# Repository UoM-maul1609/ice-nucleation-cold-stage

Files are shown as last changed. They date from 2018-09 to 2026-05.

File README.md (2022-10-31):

# Ice Nucleation Cold Stage

The Ice Nucleation Cold Stage (INCS) is a project using an Arduino and Raspberry Pi to control a Peltier module to cool and film droplets to the point where they freeze. 

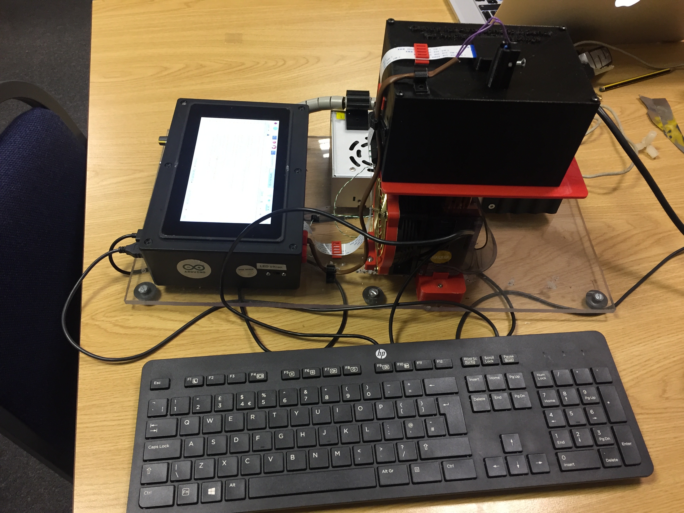
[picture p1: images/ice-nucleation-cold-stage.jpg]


<em>The Ice Nucleation Cold Stage on a desk.</em>

# Table of contents
1. [Overview](#overview)
1. [Buck Converter](#buck-conv)
2. [Dependencies](#Dependencies)
3. [Folder structure](#Folder-Structure)
5. [Contributing](#Contributing)
6. [Code of Conduct](#Code-of-Conduct)

## Overview 

The electronics fits in a project box, with a touchscreen, enabling ease of transport in the field.

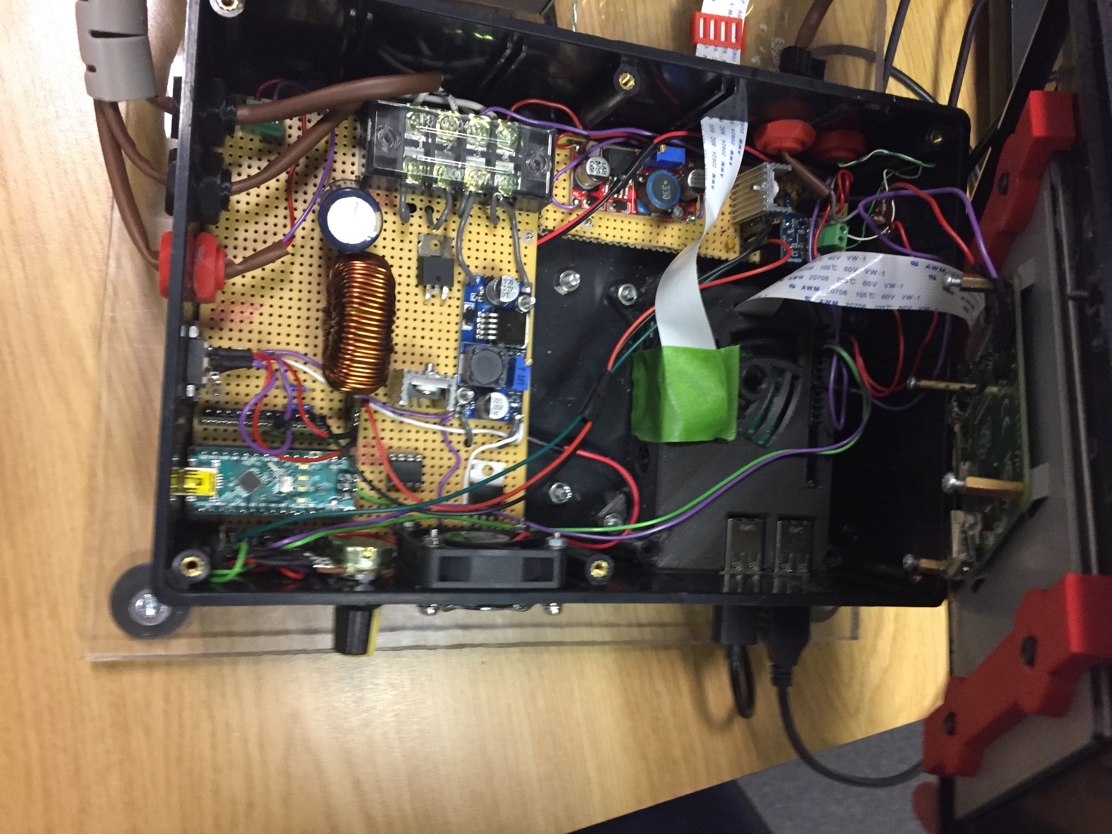
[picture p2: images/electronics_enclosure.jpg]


<em>Peltier circuit inside the project box.</em>

In addition most of the other parts are 3-d printed.

## Buck Converter 
A substantial part of this project is the buck converter circult, which is controlled by an Arduino using pulse width modulation. A buck converter is required to control the Peltier module because Peltier modules require a smooth input voltage. Pulse width modulation alone is not sufficient. 

The circuit is based on a so-called low-side switch design, meaning the MosFET switch is on the "low-side" of the load [see here](images/high_side_n_channel_buck_converter.png).

The circuit for the buck converter is shown below.

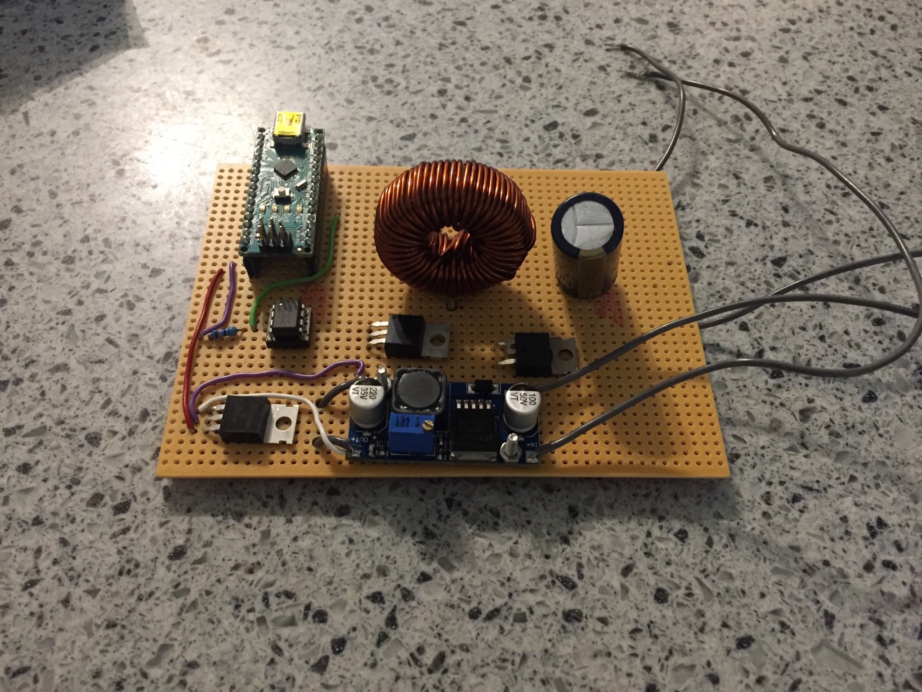
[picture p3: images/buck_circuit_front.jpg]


<em>Buck converter circuit. It consists of an Arduino Nano; a gate driver; MosFET, Inductor, Capactor, and Schottky diode. In addition there is a 3 A buck converter and linear regulator to power the arduino from a DC input.</em>

## Dependencies 

I needed to install a library for the Arduino for PID control. The library is: PID controller by Brett Beaugard. I also had to use "Wire.h" (installed by default) .for I2C communication between the Raspberry Pi and Arduino.

For the Raspberry PI the following python libraries were used: smbus; struct; time; numpy.

## Folder structure 

The repository structure is now discussed

### Directory layout

    .                           
    ├── arduino               # code for the Arduino
    ├── images                # image files for the project
    ├── links                 # some links that I used 
    ├── matlab                # matlab files (e.g. to process video to get freezing events)
    ├── openSCAD              # Design files in openSCAD
    ├── python                # Raspberry Pi files to do temperature ramps, etc
    ├── README.md             # This readme
    └── stl						# stl design files
    
----------

**REQUIRED PARTS**

In order to **make your own Ice Nucleation Cold Stage**, you may use the **part list below** to acquire all the components **on your own**. Note, although Amazon is suggested, I often used a company supplier, which was cheaper.

<table style="width:100%">
  <tr> 
    <td>
    Raspberry Pi 3 7 inch touchscreen <br>
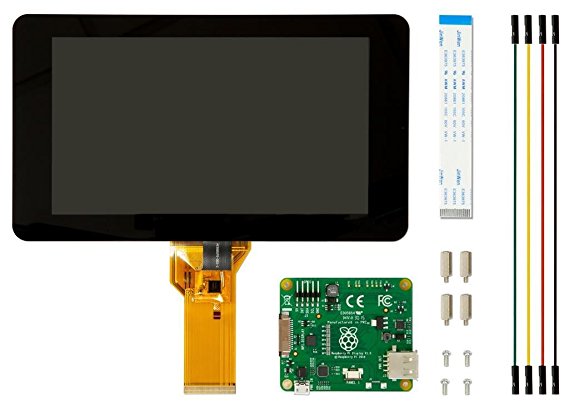
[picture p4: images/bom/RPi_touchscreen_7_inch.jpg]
    </td>
    <td><a href="https://www.amazon.co.uk/Raspberry-Pi-7-Inch-Screen-Display/dp/B014WKCFR4/ref=sr_1_3?ie=UTF8&qid=1531558042&sr=8-3&keywords=raspberry+pi+touch+screen+7+inch" target="_blank"> Amazon </a></td> 
    <td>£63</td>
  </tr>
  
  <tr> 
    <td>
    Raspberry Pi 3 b+ <br>
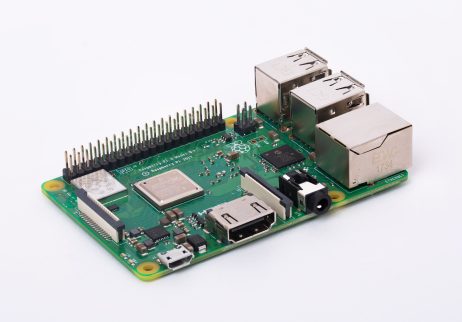
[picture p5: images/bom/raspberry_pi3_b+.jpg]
    </td>
    <td><a href="https://www.amazon.co.uk/Raspberry-Pi-Model-64-Bit-Processor/dp/B07BDR5PDW/ref=sr_1_3?ie=UTF8&qid=1531556638&sr=8-3&keywords=raspberry-pi+3+b" target="_blank"> Amazon </a></td> 
    <td>£35</td>
  </tr>
  
  <tr> 
    <td>
    Raspberry Pi Camera Board 8 Megapixel Version 2 1080p <br>
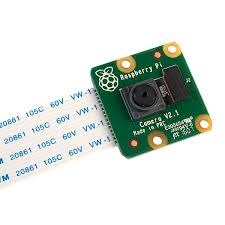
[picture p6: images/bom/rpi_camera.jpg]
    </td>
    <td><a href="https://www.rapidonline.com/raspberry-pi-camera-board-8-megapixel-version-2-1080p-75-0530" target="_blank"> Rapid Online </a></td> 
    <td>£23.70</td>
  </tr>

  <tr>
    <td>
    Arduino Nano A000005 Board V3<br>
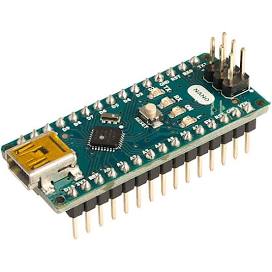
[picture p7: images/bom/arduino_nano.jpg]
    </td>
    <td><a href="https://www.rapidonline.com/arduino-nano-a000005-board-v3-73-4448" target="_blank"> Rapid Electronics </a></td> 
    <td>£15.60</td>
  </tr>

  <tr>
    <td>
    2.54mm Pitch Vertical 8 Way, Through Hole Turned pin Open Frame IC Dip Socket, 5A<br>
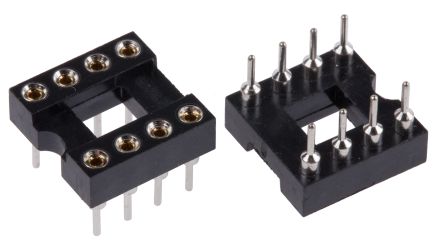
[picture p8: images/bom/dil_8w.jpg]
    </td>
    <td><a href="https://uk.rs-online.com/web/p/dil-sockets/0813115/" target="_blank"> RS Components </a></td> 
    <td>£0.38</td>
  </tr>

  <tr>
    <td>
    Rapid Stripboard 95 x 127mm (x2)<br>
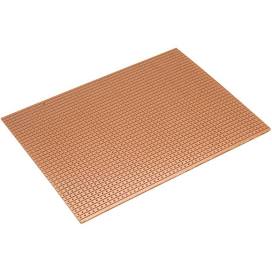
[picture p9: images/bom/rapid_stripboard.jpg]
    </td>
    <td><a href="https://www.rapidonline.com/rapid-stripboard-95-x-127mm-34-0515" target="_blank"> Rapid Online </a></td> 
    <td>£3.84</td>
  </tr>

  <tr>
    <td>
    2200 uF capactor, 35V.<br>
    </td>
    <td><a href="https://uk.farnell.com/panasonic-electronic-components/eca1vhg222/cap-alu-elec-2200uf-35v-rad/dp/1848552?st=CAPACITOR,%202200UF%2035V;%20Automotive%20Qualification%20Standard:AEC-Q200" target="_blank"> Farnell </a></td> 
    <td>£1.27</td>
  </tr>

  <tr>
    <td>
    470 µH, 7A, 0.064 ohm, ± 20%, Inductor<br>
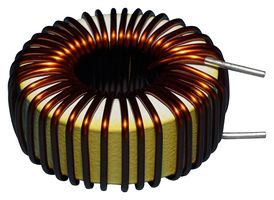
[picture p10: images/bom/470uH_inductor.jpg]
    </td>
    <td><a href="https://uk.farnell.com/abracon/atca-08-471m-v/inductor-470uh-7a-20-radial/dp/2665051?krypto=pY3JNPCYatNk0vDDUf4Tn9JLFiz93rvd2B4Xt3Ip1h5SCi3yEomoX%2BUEleAGflP2kAMSJSf9N%2FZLG3PFYvM%2Bmw%3D%3D&ddkey=https%3Aen-GB%2FElement14_United_Kingdom%2Fsearch" target="_blank"> Farnell </a></td> 
    <td>£9.89</td>
  </tr>

  <tr>
    <td>
    IRF520NPBF -  MOSFET Transistor, N Channel <br>
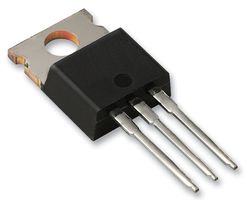
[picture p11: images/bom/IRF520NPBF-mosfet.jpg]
    </td>
    <td><a href="https://uk.farnell.com/infineon/irf520npbf/mosfet-n-100v-9-7a-to-220ab/dp/9103031" target="_blank"> Farnell </a></td> 
    <td>£0.65</td>
  </tr>

  <tr>
    <td>
    VS-15TQ060PBF -  Schottky Rectifier <br>
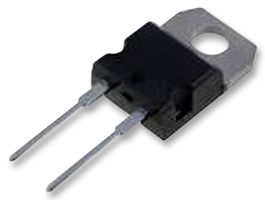
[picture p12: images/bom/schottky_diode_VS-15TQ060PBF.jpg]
    </td>
    <td><a href="https://uk.farnell.com/vishay-semiconductor/vs-15tq060pbf/diode-schottky-15a-60v-to-220ac/dp/8657009" target="_blank"> Farnell </a></td> 
    <td>£2.05</td>
  </tr>

  <tr>
    <td>
    Cooler Master Hyper TX (RR-PCH-s9U1-GP) <br>
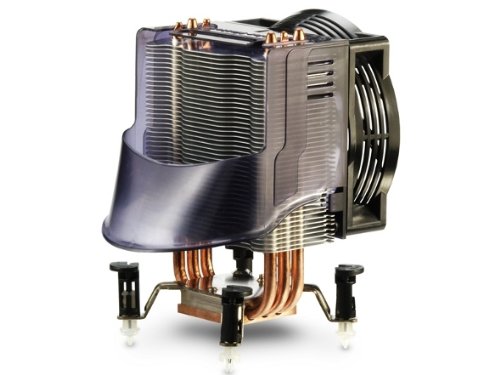
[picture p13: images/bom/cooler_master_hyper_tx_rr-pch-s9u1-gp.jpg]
    </td>
    <td><a href="https://www.amazon.co.uk/Cooler-Master-Socket-775-650-1800RPM-41-76-CFM/dp/B000K0ZSH0" target="_blank"> This was given to me. It is discontinued, but any similar heat sink could be used (e.g. the Cooler Master Hyper TX3i) </a></td> 
    <td>approx. £30</td>
  </tr>

  <tr>
    <td>
    mc34152 Gate Driver <br>
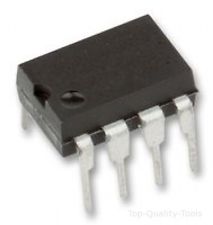
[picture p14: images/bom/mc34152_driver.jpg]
    </td>
    <td><a href="https://uk.rs-online.com/web/p/mosfet-power-drivers/5165506/" target="_blank"> RS Components </a></td> 
    <td>£1.15</td>
  </tr>

  <tr>
    <td>
    Enclosure <br>
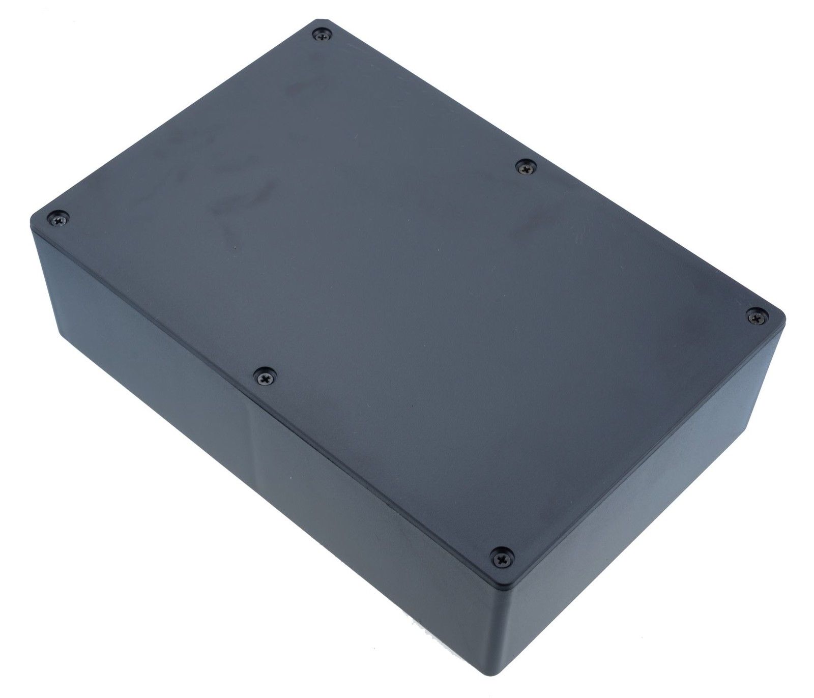
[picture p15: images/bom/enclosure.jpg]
    </td>
    <td><a href="https://www.ebay.co.uk/itm/1591XXFSBK-Genuine-Hammond-Black-ABS-Enclosure-Box-221-x-150-x-63mm/262220045766?hash=item3d0d885dc6:g:-PkAAOSw1BlZVgdG" target="_blank"> Ebay </a></td> 
    <td>£10</td>
  </tr>

  <tr>
    <td>
    Micro SD card<br>
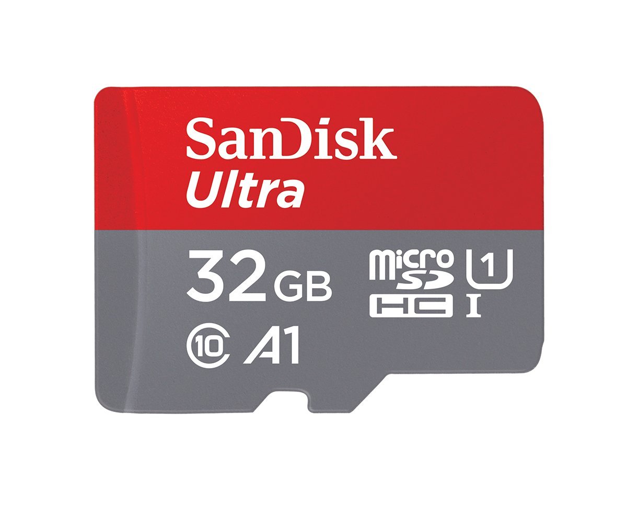
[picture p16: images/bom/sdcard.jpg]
    </td>
    <td><a href="https://www.amazon.co.uk/gp/offer-listing/B073JWXGNT/ref=sr_1_5_olp?s=electronics-accessories&ie=UTF8&qid=1531613685&sr=1-5&keywords=micro+sd+card" target="_blank"> Amazon </a></td> 
    <td>£8</td>
  </tr>

  <tr>
    <td>
    2 Pin 5 mm Pinch PCB Mount Screw Terminal Block Connector<br>
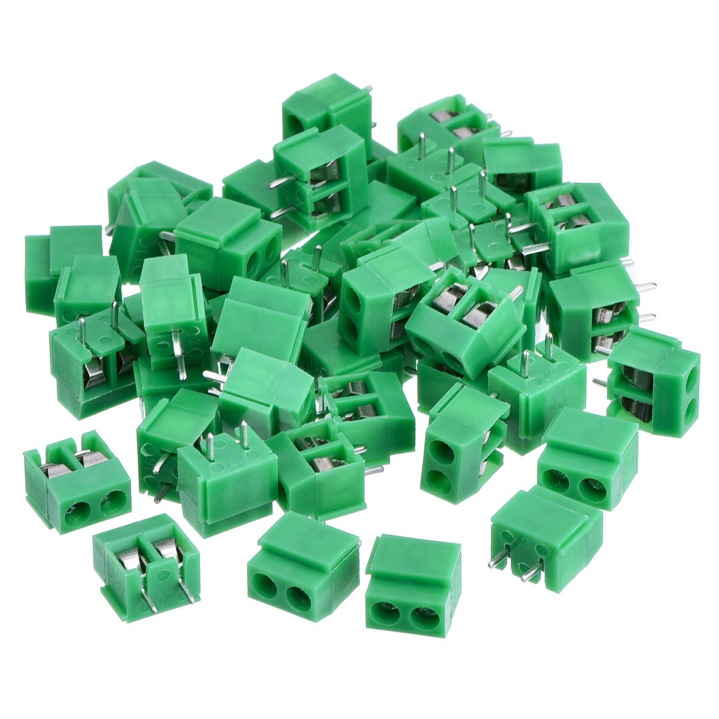
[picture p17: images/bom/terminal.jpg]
    </td>
    <td><a href="https://www.amazon.co.uk/gp/product/B01MT4LC0F/ref=oh_aui_detailpage_o03_s00?ie=UTF8&psc=1" target="_blank"> Amazon </a></td> 
    <td>£6</td>
  </tr>

  <tr>
    <td>
    Buck converter <br>
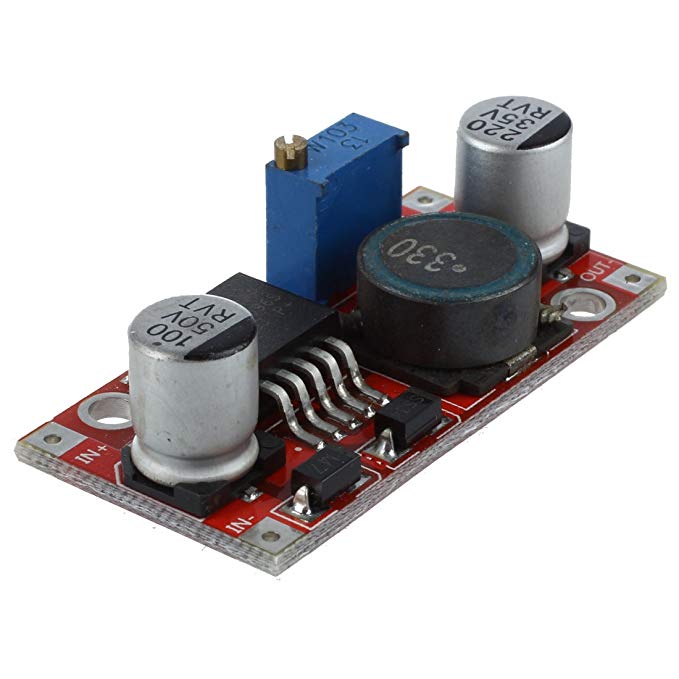
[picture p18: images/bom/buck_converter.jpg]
    </td>
    <td><a href="https://www.amazon.co.uk/gp/product/B00K67XSYC/ref=oh_aui_detailpage_o06_s00?ie=UTF8&psc=1" target="_blank"> Amazon </a></td> 
    <td>£8</td>
  </tr>

  <tr>
    <td>
    Linear regulator 10V, 1A<br>
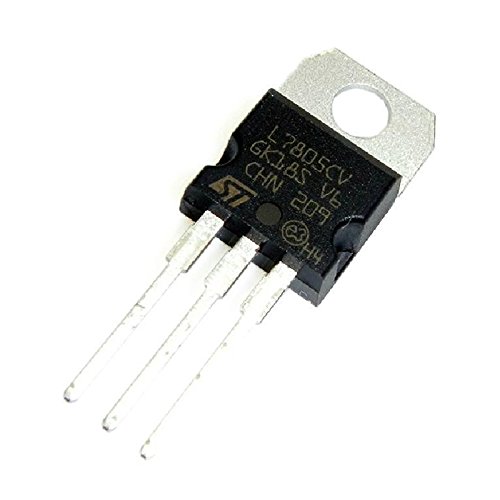
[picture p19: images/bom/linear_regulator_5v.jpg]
    </td>
    <td><a href="https://uk.farnell.com/on-semiconductor/ka7810etu/linear-volt-reg-1a-10v-to-220ab/dp/2451046" target="_blank"> Farnell </a></td> 
    <td>£3</td>
  </tr>
  
  <tr>
    <td>
    Slide switch <br>
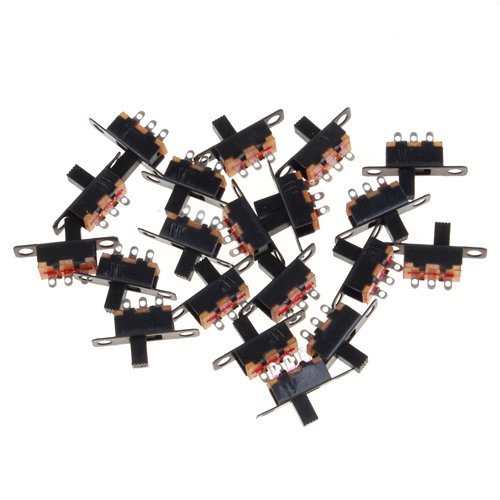
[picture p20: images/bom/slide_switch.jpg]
    </td>
    <td><a href="https://www.amazon.co.uk/gp/product/B008R50AA0/ref=oh_aui_detailpage_o07_s00?ie=UTF8&psc=1" target="_blank"> Amazon </a></td> 
    <td>£0.15</td>
  </tr>
  
  <tr>
    <td>
    PCB Header Connectors <br>
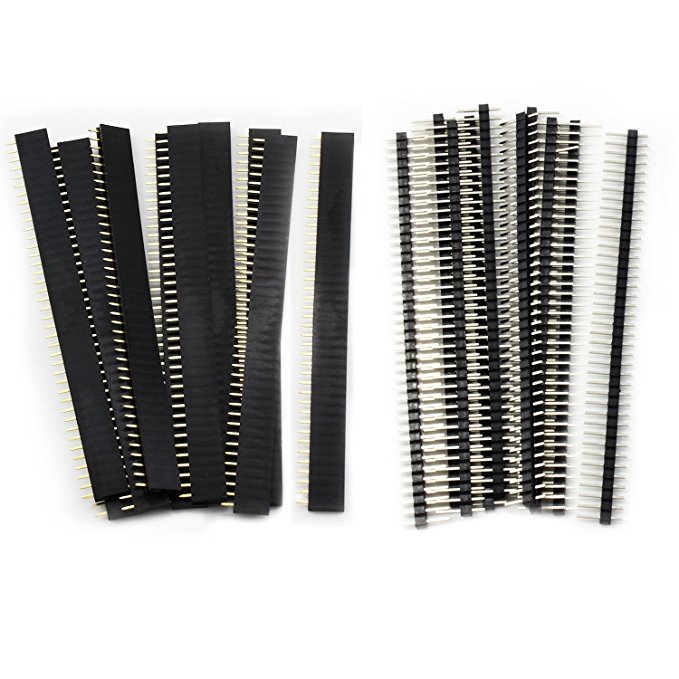
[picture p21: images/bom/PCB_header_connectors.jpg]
    </td>
    <td><a href="https://www.amazon.co.uk/gp/product/B01M69EA9O/ref=oh_aui_detailpage_o03_s00?ie=UTF8&psc=1" target="_blank"> Amazon </a></td> 
    <td>£5</td>
  </tr>
  
  <tr>
    <td>
    Dupoint wires <br>
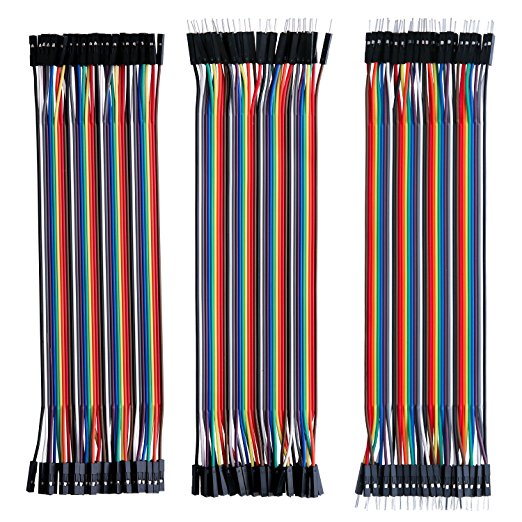
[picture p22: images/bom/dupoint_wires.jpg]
    </td>
    <td><a href="https://www.amazon.co.uk/gp/product/B01EV70C78/ref=oh_aui_detailpage_o04_s00?ie=UTF8&psc=1" target="_blank"> Amazon </a></td> 
    <td>£6</td>
  </tr>
  
  <tr>
    <td>
    20AWG Wire <br>
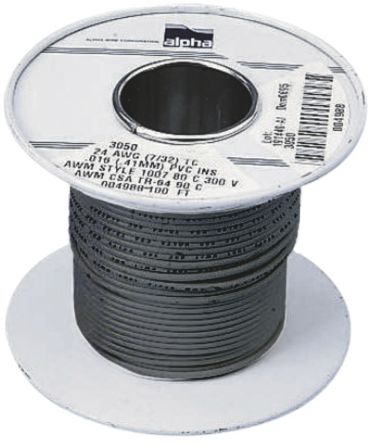
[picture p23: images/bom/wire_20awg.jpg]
    </td>
    <td><a href="https://uk.rs-online.com/web/p/hookup-equipment-wire/0331935/?relevancy-data=636F3D3126696E3D4931384E525353746F636B4E756D626572266C753D656E266D6D3D6D61746368616C6C26706D3D5E282872737C5253295B205D3F293F2832355C647B387D7C32355C647B317D5C2D5C647B377D7C5C647B337D5B5C2D5D3F5C647B332C347D5B70505D3F292426706F3D3126736E3D592673723D2673743D52535F53544F434B5F4E554D4245522677633D4E4F4E45267573743D333331393335267374613D3033333139333526" target="_blank"> RS Online </a></td> 
    <td>£13.03</td>
  </tr>
  
  <tr>
    <td>
    Affix Pozi Pan Head Stainless Steel Screws M2.5 12mm  <br>
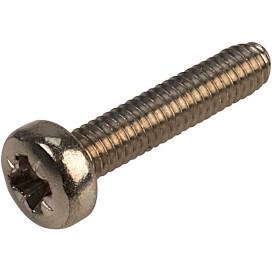
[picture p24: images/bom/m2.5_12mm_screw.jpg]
    </td>
    <td><a href="https://www.rapidonline.com/Affix-Pozi-Pan-Head-Stainless-Steel-Screws-M2-5-12mm-Pack-Of-100-33-4205?utm_source=AffWin&utm_medium=Affiliate&awc=1799_1531559350_6bf53c34df454762e1e501399281f666" target="_blank"> Rapid online </a></td> 
    <td>£3.40</td>
  </tr>
  
  <tr>
    <td>
    Affix Stainless Steel Plain Washers M2.5  <br>
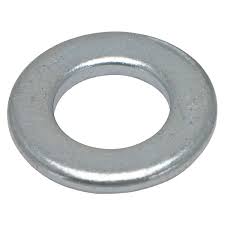
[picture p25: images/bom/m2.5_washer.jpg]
    </td>
    <td><a href="https://www.rapidonline.com/affix-stainless-steel-plain-washers-m2-5-pack-of-100-33-4315" target="_blank"> Rapid online </a></td> 
    <td>£1</td>
  </tr>
  
  <tr>
    <td>
    M2.5 nuts <br>
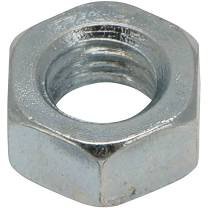
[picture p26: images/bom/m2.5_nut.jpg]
    </td>
    <td><a href="https://www.rapidonline.com/tr-fastenings-w-m2-5-hfst-tc1-steel-full-nuts-metric-m2-5-box-of-100-33-6589" target="_blank"> Rapid online </a></td> 
    <td>£1.20</td>
  </tr>
  
  <tr>
    <td>
    Potentiometer <br>
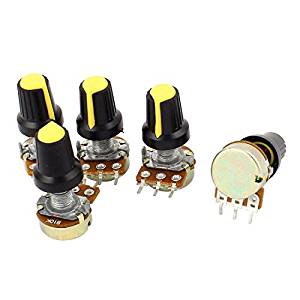
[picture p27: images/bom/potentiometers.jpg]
    </td>
    <td><a href="https://www.amazon.co.uk/gp/product/B01G6P1H68/ref=oh_aui_detailpage_o07_s00?ie=UTF8&psc=1" target="_blank"> Amazon </a></td> 
    <td>£1.27 for 5</td>
  </tr>
  
  <tr>
    <td>
    Terminal Blocks <br>
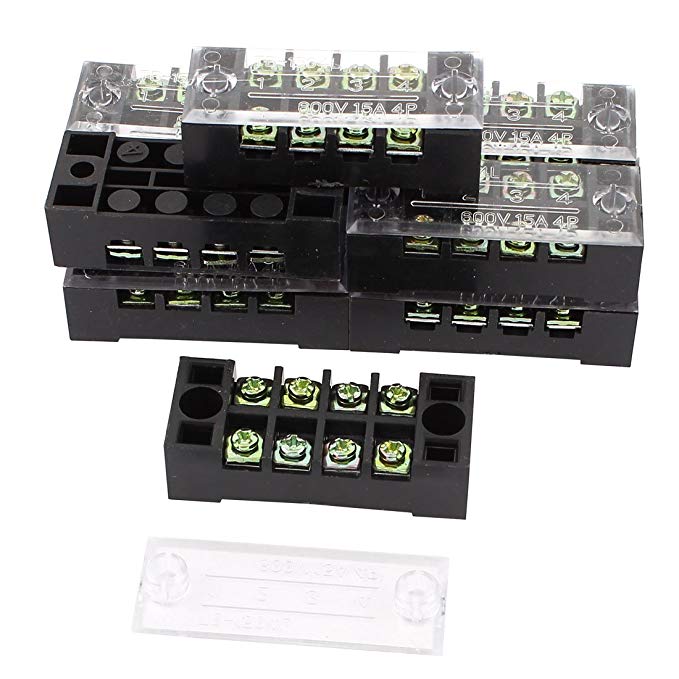
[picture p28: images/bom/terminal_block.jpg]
    </td>
    <td><a href="https://www.amazon.co.uk/gp/product/B00O9W183I/ref=oh_aui_detailpage_o01_s00?ie=UTF8&psc=1" target="_blank"> Amazon </a></td> 
    <td>£6.32 for 10</td>
  </tr>
  
  <tr>
    <td>
    Fuses for DC Power supply <br>
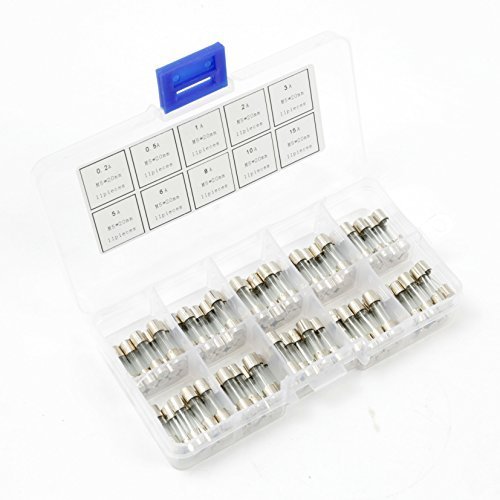
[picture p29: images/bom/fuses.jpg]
    </td>
    <td><a href="https://www.amazon.co.uk/gp/product/B01CEB6B1Y/ref=oh_aui_detailpage_o04_s00?ie=UTF8&psc=1" target="_blank"> Amazon </a></td> 
    <td>£5.29 for many!</td>
  </tr>
  
  <tr>
    <td>
    Raspberry Pi camera cable, 50cm <br>
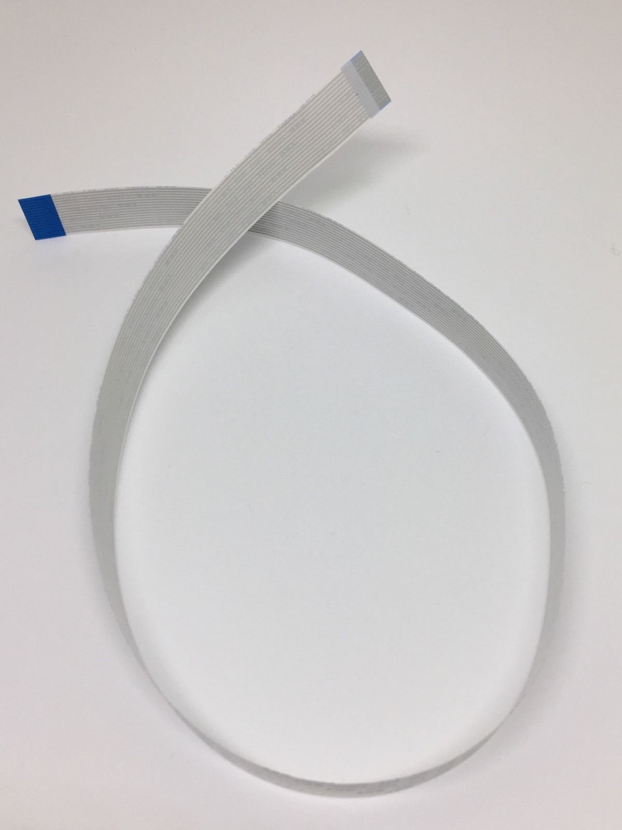
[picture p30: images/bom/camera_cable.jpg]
    </td>
    <td><a href="https://www.ebay.co.uk/itm/Raspberry-Pi-Camera-Cable-50-cm/152700214804?ssPageName=STRK%3AMEBIDX%3AIT&_trksid=p2057872.m2749.l2649" target="_blank"> Ebay </a></td> 
    <td>£1.20</td>
  </tr>
  
  <tr>
    <td>
    AD8495 thermocouple <br>
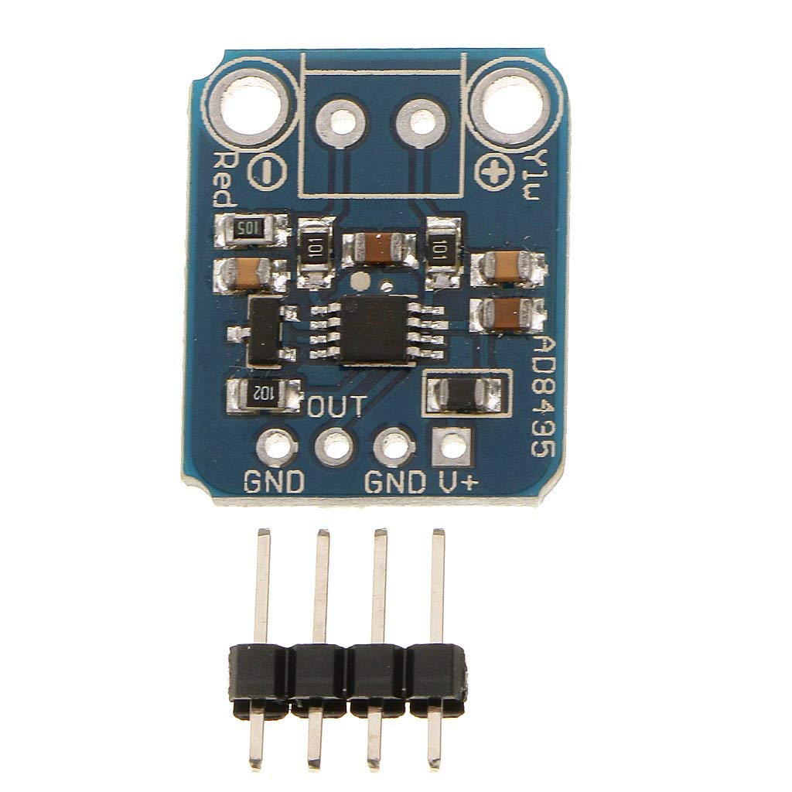
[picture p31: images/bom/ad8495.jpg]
    </td>
    <td><a href="https://www.amazon.co.uk/gp/product/B0744M3DQD/ref=oh_aui_search_detailpage?ie=UTF8&psc=1" target="_blank"> Amazon </a></td> 
    <td>£4.99</td>
  </tr>
  
  <tr>
    <td>
    Heat sinks for mosFET and 5V linear regulator. <br>
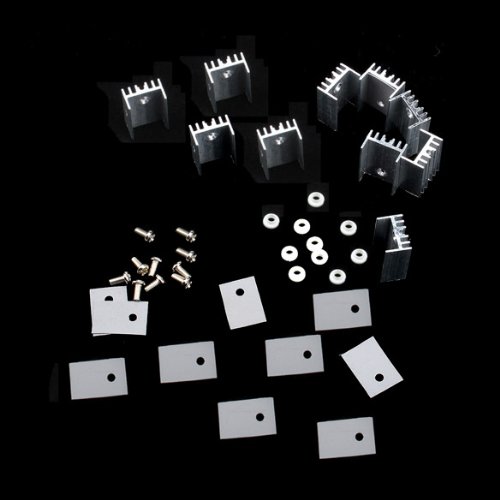
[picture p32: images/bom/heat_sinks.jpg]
    </td>
    <td><a href="https://www.amazon.co.uk/gp/product/B01IN11NWG/ref=oh_aui_detailpage_o02_s00?ie=UTF8&psc=1" target="_blank"> Amazon </a></td> 
    <td>£2.00</td>
  </tr>
  
  <tr>
    <td>
    24V, 15A Universal Regulated Switching Power Supply. <br>
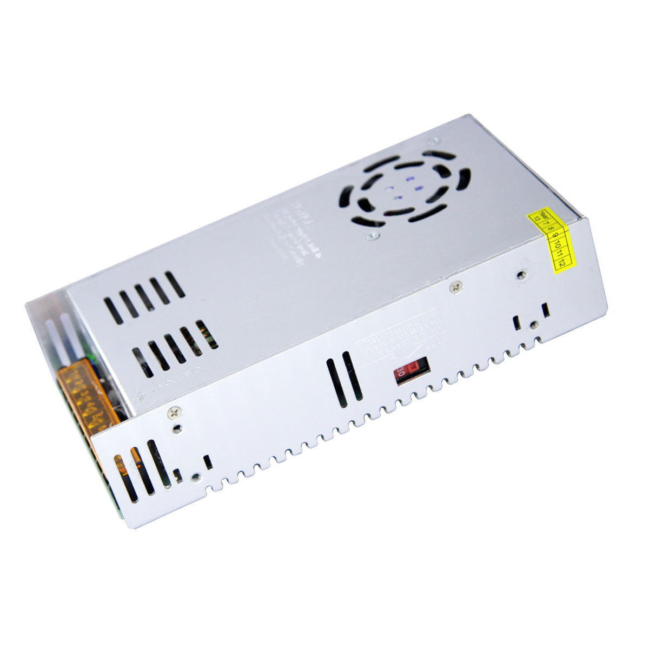
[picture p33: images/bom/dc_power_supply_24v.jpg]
    </td>
    <td><a href="https://www.ebay.co.uk/itm/DC-5-12-24V-Universal-Regulated-Switching-Power-Supply-for-LED-Strip-CCTV-UK-/172578089978?oid=183217277720" target="_blank"> Ebay </a></td> 
    <td>£13.59</td>
  </tr>
  
  <tr>
    <td>
    3 Pin IEC320 C14 Inlet Module. <br>
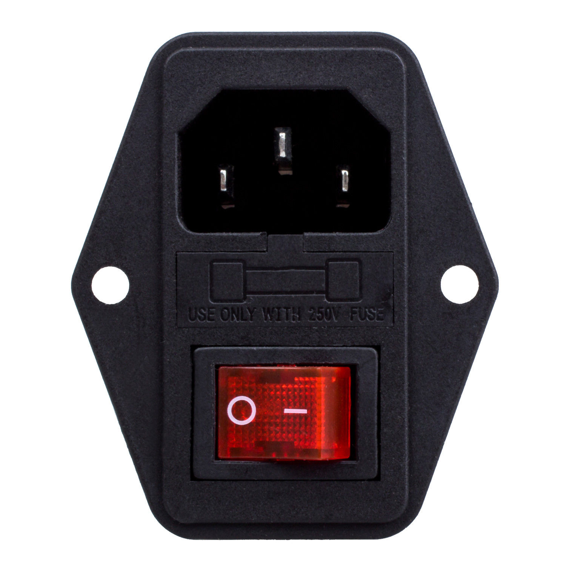
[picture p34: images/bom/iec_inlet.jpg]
    </td>
    <td><a href="https://www.ebay.co.uk/itm/3-Pin-IEC320-C14-Inlet-Module-Plug-Fuse-Switch-Male-Power-Socket-10A-250V-L5V1-/282655120864" target="_blank"> Ebay </a></td> 
    <td>£1.01</td>
  </tr>
  
  <tr>
    <td>
    3.5mm Pitch 2Pin PCB Mount Screw Terminal Block Connector. <br>
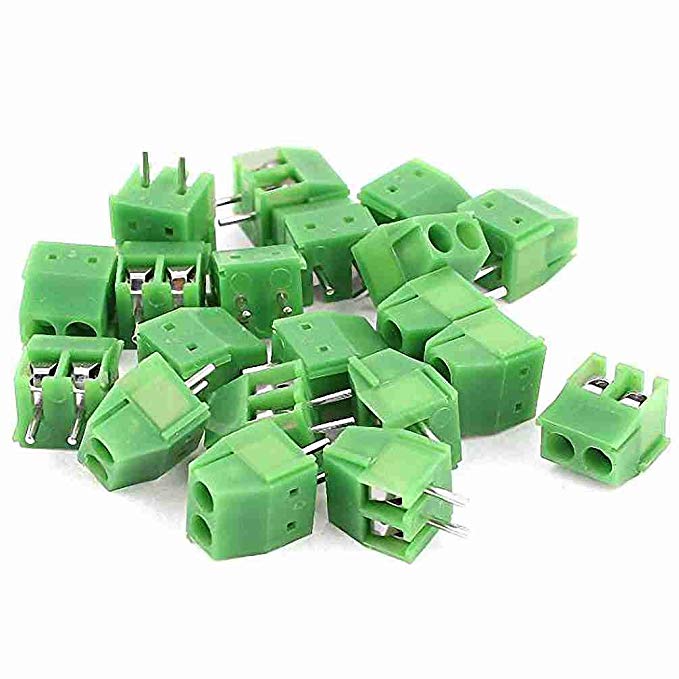
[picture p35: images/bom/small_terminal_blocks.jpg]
    </td>
    <td><a href="https://www.amazon.co.uk/gp/product/B00XL5BMP8/ref=oh_aui_search_detailpage?ie=UTF8&psc=1" target="_blank"> Amazon </a></td> 
    <td>£2.94</td>
  </tr>
  
  <tr>
    <td>
    10 Metres 4mm Brown Sleeving On A Roll. <br>
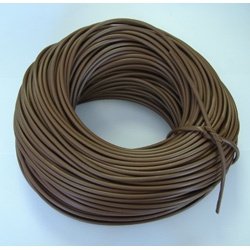
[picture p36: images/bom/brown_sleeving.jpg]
    </td>
    <td><a href="https://www.amazon.co.uk/gp/product/B006I1K7NU/ref=oh_aui_search_detailpage?ie=UTF8&psc=1" target="_blank"> Amazon </a></td> 
    <td>£2.99</td>
  </tr>

  <tr>
    <td>
    40 mm fan guard <br>
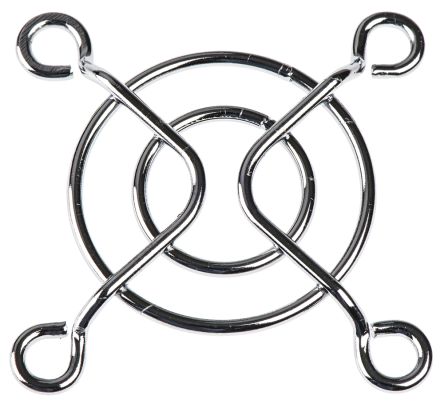
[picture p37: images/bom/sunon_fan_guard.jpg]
    </td>
    <td><a href="https://www.rapidonline.com/SUNON-FG-04-Fan-Grill-40mm-x-40mm-50-5138?IncVat=1&pdg=aud-313476735010:pla-336800058227:kwd-336800058227:cmp-757438067:adg-44804851896:crv-207912323492:pid-50-5138:dev-c&gclid=Cj0KCQjwv-DaBRCcARIsAI9sba88Hs9De4c6fpl-Nrf_ln1wQZMeWvz_mbl0ramittN_1RAl-sdb2TAaAj1EEALw_wcB" target="_blank"> Rapid electronics</a> <br> Or Part No: 50-5136. SUNON FG-04 Fan Grill</td> 
    <td>£3.50</td>
  </tr>

  <tr>
    <td>
    40 mm fan <br>
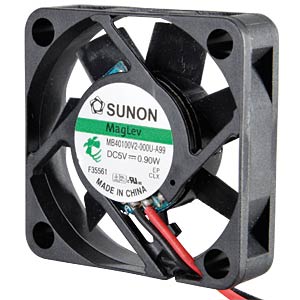
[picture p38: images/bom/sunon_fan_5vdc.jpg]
    </td>
    <td><a href="https://www.reichelt.com/gb/en/fan-5-v-dc-0-9-w-rpm-5800-fan-4010-5v-p43677.html?CTYPE=0&MWSTFREE=0&PROVID=2788&wt_guka=54951061155_263550072470&PROVID=2788&gclid=Cj0KCQjwv-DaBRCcARIsAI9sba-WNEJHtybDi85atG_sroZEsvyVNrddHD7doeqlnKYRUztaJ6kxCHgaAnc5EALw_wcB&" target="_blank"> Reichelt electronics </a><br> Or SUNON EE40100S1-00U-999 DRR / 50-5096
</td>     <td>£2.50</td>
  </tr>
  
  <tr>
    <td>
    550 x 250 x 8 mm perspex sheet (clear) <br>
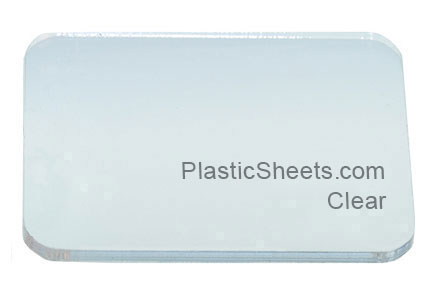
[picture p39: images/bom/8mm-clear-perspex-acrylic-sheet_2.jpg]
    </td>
    <td><a href="http://www.plasticsheets.com/?gclid=Cj0KCQjwx43ZBRCeARIsANzpzb9o_f5blJqmZOe1sliMkC1TyBPAPn1GouSZxKyQbyZHcnOesRTrROwaArQVEALw_wcB" target="_blank"> Plastic sheets </a></td> 
    <td>£12.38</td>
  </tr>
  
  <tr>
    <td>
    LED <br>
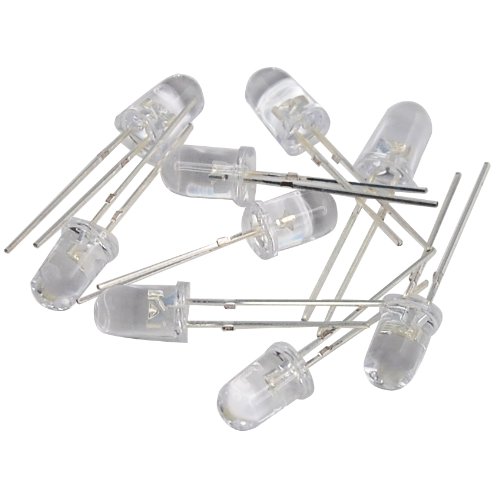
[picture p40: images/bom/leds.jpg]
    </td>
    <td><a href="https://www.amazon.co.uk/dp/B00CM5DEZO/ref=sxts_kp_lp_3?pf_rd_m=A3P5ROKL5A1OLE&pf_rd_p=fb7bbe16-4a21-4f5a-938c-e2ac1558fbcd&pd_rd_wg=WvUCM&pf_rd_r=G8N068HW8BDFM7DW6CEY&pf_rd_s=desktop-sx-top-slot&pf_rd_t=301&pd_rd_i=B00CM5DEZO&pd_rd_w=RxAWr&pf_rd_i=leds&pd_rd_r=ad3598ab-370e-4f6e-a6e7-f164199962c9&ie=UTF8&qid=1535959984&sr=3" target="_blank"> Amazon </a></td> 
    <td>£0.65</td>
  </tr>
  
  <tr>
    <td>
    IEC Cable <br>
    </td>
    <td><a href="https://uk.rs-online.com/web/p/power-cable-assemblies/2621154/" target="_blank"> RS Components </a></td> 
    <td>£6.50</td>
  </tr>
  
  <tr>
    <td>
    Peltier Element, 16V, 7.8A <br>
    </td>
    <td><a href="https://uk.farnell.com/european-thermodynamics/ap2-162-1420-1118/peltier-cooler-module-16vdc-29/dp/2519563" target="_blank"> Farnell </a></td> 
    <td>£99.89</td>
  </tr>
  
  <tr>
    <td>
    25x25mm microscope slides <br>
    </td>
    <td><a href="https://www.fishersci.co.uk/shop/products/microscope-slides-cut-square-13/15522802?searchHijack=true&searchTerm=15522802&searchType=RAPID&matchedCatNo=15522802" target="_blank"> Fisher </a></td> 
    <td>£30.76 exc VAT for 1000</td>
  </tr>

  <tr>
    <td>
    0.1 uF capacitor <br>
    </td>
    <td><a href="https://uk.rs-online.com/web/p/ceramic-multilayer-capacitors/8523299/?relevancy-data=636F3D3126696E3D4931384E525353746F636B4E756D626572266C753D656E266D6D3D6D61746368616C6C26706D3D5E282872737C5253295B205D3F293F2832355C647B387D7C32355C647B317D5C2D5C647B377D7C5C647B337D5B5C2D5D3F5C647B332C347D5B70505D3F292426706F3D3126736E3D592673723D2673743D52535F53544F434B5F4E554D4245522677633D4E4F4E45267573743D38353233323939267374613D3835323332393926" target="_blank"> RS Components </a></td> 
    <td>£1.00</td>
  </tr>
  
  <tr>
    <td>
    1 uF tantalum capacitor <br>
    </td>
    <td><a href="https://www.rapidonline.com/Catalogue/Product/11-1036" target="_blank"> Rapid Online </a></td> 
    <td>£0.27</td>
  </tr>
  
  <tr>
    <td>
    Affix Black Pozi Pan Head Machine Screws M3 12mm - Pack Of 100 <br>
    </td>
    <td><a href="https://www.rapidonline.com/Catalogue/Product/33-2630" target="_blank"> Rapid Online </a></td> 
    <td>£1.55</td>
  </tr>
  
  <tr>
    <td>
    Affix Slotted Countersunk Machine Screws BZP M4 16mm - Pack Of 100 <br>
    </td>
    <td><a href="https://www.rapidonline.com/Catalogue/Product/33-2885" target="_blank"> Rapid Online </a></td> 
    <td>£1.58</td>
  </tr>
  
  <tr>
    <td>
    Affix Pozi Countersunk Machine Screws BZP M4 12mm - Pack Of 100 <br>
    </td>
    <td><a href="https://www.rapidonline.com/Catalogue/Product/33-2970" target="_blank"> Rapid Online </a></td> 
    <td>£2.47</td>
  </tr>
  
  <tr>
    <td>
    Toolcraft 193152 Slotted Countersunk Screws DIN 963 4.8 Steel M4x20mm Pk 100 <br>
    </td>
    <td><a href="https://www.rapidonline.com/Catalogue/Product/51-3237" target="_blank"> Rapid Online </a></td> 
    <td>£4.78</td>
  </tr>

  <tr>
    <td>
    Affix Stainless Steel Nuts M4 - Pack Of 100 <br>
    </td>
    <td><a href="https://www.rapidonline.com/Catalogue/Product/33-4310" target="_blank"> Rapid Online </a></td> 
    <td>£3.00</td>
  </tr>

  <tr>
    <td>
    LIGHTWEIGHT ZINC EFFECT METAL BUTT HINGE, PACK OF 2 <br>
    </td>
    <td><a href="https://www.diy.com/departments/lightweight-zinc-effect-metal-butt-hinge-pack-of-2/254482_BQ.prd" target="_blank"> B&Q </a></td> 
    <td>£1.47</td>
  </tr>

  <tr>
    <td>
    Linear regulator <br>
    </td>
    <td><a href="https://www.amazon.co.uk/LM338T-Adjustable-Positive-Voltage-Regulator/dp/B07F2YMXTR/ref=sr_1_cc_1?s=aps&ie=UTF8&qid=1531560057&sr=1-1-catcorr&keywords=lm338" target="_blank"> Amazon </a></td> 
    <td>£3</td>
  </tr>

  <tr>
    <td>
    5pcs 90 x 90mm Cooling Fan Grill Metal Iron Wire Finger Guards System Pack (only need one) <br>
    </td>
    <td><a href="https://cgi.ebay.co.uk/ws/eBayISAPI.dll?ViewItemVersion&item=292531055201&view=all&tid=1589736431019" target="_blank"> Ebay </a></td> 
    <td>£1.96</td>
  </tr>

</table>

Plus: 
<ul>
<li> Resistors: 680 &Omega; ;2x220 &Omega; ;50 k &Omega;
<li> USB keyboard and mouse; 
<li> M4 washers (already had some)
<li> M4 rod for screwing down cover (already had some)
<li> some other wire 22awg for low current connections;  
<li> some thermocouple wire (K-type).
<li> Spade connectors.
<li> 240V cable (usually butcher a spare IEC cable with a US plug).
<li> 3-d printing materials:
	<ul>
	<li> ABS plastic
	<li> PLA plastic
	<li> TPU plastic
	</ul>
</ul>

## Contributing

Contributions to INCS are more than welcome. I am sure there are many improvements that could be made. I am very happy to discuss ideas for improvement and how to add/remove features.  

Please use the issue tracker at https://github.com/UoM-maul1609/ice-nucleation-cold-stage/issues if you want to notify me of an issue or need support. If you want to contribute, please either create an issue or make a pull request. Alternatively, come and see me in Manchester and/or lets meet for a coffee and a chat!

## Code of Conduct

To be arranged.

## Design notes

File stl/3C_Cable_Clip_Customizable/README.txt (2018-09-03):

                   .:                     :,                                          
,:::::::: ::`      :::                   :::                                          
,:::::::: ::`      :::                   :::                                          
.,,:::,,, ::`.:,   ... .. .:,     .:. ..`... ..`   ..   .:,    .. ::  .::,     .:,`   
   ,::    :::::::  ::, :::::::  `:::::::.,:: :::  ::: .::::::  ::::: ::::::  .::::::  
   ,::    :::::::: ::, :::::::: ::::::::.,:: :::  ::: :::,:::, ::::: ::::::, :::::::: 
   ,::    :::  ::: ::, :::  :::`::.  :::.,::  ::,`::`:::   ::: :::  `::,`   :::   ::: 
   ,::    ::.  ::: ::, ::`  :::.::    ::.,::  :::::: ::::::::: ::`   :::::: ::::::::: 
   ,::    ::.  ::: ::, ::`  :::.::    ::.,::  .::::: ::::::::: ::`    ::::::::::::::: 
   ,::    ::.  ::: ::, ::`  ::: ::: `:::.,::   ::::  :::`  ,,, ::`  .::  :::.::.  ,,, 
   ,::    ::.  ::: ::, ::`  ::: ::::::::.,::   ::::   :::::::` ::`   ::::::: :::::::. 
   ,::    ::.  ::: ::, ::`  :::  :::::::`,::    ::.    :::::`  ::`   ::::::   :::::.  
                                ::,  ,::                               ``             
                                ::::::::                                              
                                 ::::::                                               
                                  `,,`

https://www.thingiverse.com/thing:2185517
3C Cable Clip Customizable by frol is licensed under the Creative Commons - Attribution license.
http://creativecommons.org/licenses/by/3.0/

# Summary

3C clips - a set of customizable cable clips.

You can easily create clips of your own sizes [in Customizer](http://www.thingiverse.com/apps/customizer/run?thing_id=2185517).

Update 2017-03-23: Added a cable to rod clip variant.
Update 2017-05-13: More clip variants, some parameters are determined automatically (but can be overridden).

# Print Settings

Rafts: No
Supports: No

Notes: 
Twisted double clip may require support for printing, other variants print without support

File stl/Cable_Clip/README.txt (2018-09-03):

                   .:                     :,                                          
,:::::::: ::`      :::                   :::                                          
,:::::::: ::`      :::                   :::                                          
.,,:::,,, ::`.:,   ... .. .:,     .:. ..`... ..`   ..   .:,    .. ::  .::,     .:,`   
   ,::    :::::::  ::, :::::::  `:::::::.,:: :::  ::: .::::::  ::::: ::::::  .::::::  
   ,::    :::::::: ::, :::::::: ::::::::.,:: :::  ::: :::,:::, ::::: ::::::, :::::::: 
   ,::    :::  ::: ::, :::  :::`::.  :::.,::  ::,`::`:::   ::: :::  `::,`   :::   ::: 
   ,::    ::.  ::: ::, ::`  :::.::    ::.,::  :::::: ::::::::: ::`   :::::: ::::::::: 
   ,::    ::.  ::: ::, ::`  :::.::    ::.,::  .::::: ::::::::: ::`    ::::::::::::::: 
   ,::    ::.  ::: ::, ::`  ::: ::: `:::.,::   ::::  :::`  ,,, ::`  .::  :::.::.  ,,, 
   ,::    ::.  ::: ::, ::`  ::: ::::::::.,::   ::::   :::::::` ::`   ::::::: :::::::. 
   ,::    ::.  ::: ::, ::`  :::  :::::::`,::    ::.    :::::`  ::`   ::::::   :::::.  
                                ::,  ,::                               ``             
                                ::::::::                                              
                                 ::::::                                               
                                  `,,`

https://www.thingiverse.com/thing:2987499
Cable Clip by grumbel is licensed under the Creative Commons - Attribution license.
http://creativecommons.org/licenses/by/3.0/

# Summary

Tiny cable clip (1x2cm) with a flat base, useful for holding USB cables to the table. Meant to be used in combination with double sided tape (e.g. 3M VHB), not screws. Needs to be printed laying on it's side, otherwise it will break from layer separation when flexed. Use 100% infill.

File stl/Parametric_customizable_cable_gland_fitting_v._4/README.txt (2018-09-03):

                   .:                     :,                                          
,:::::::: ::`      :::                   :::                                          
,:::::::: ::`      :::                   :::                                          
.,,:::,,, ::`.:,   ... .. .:,     .:. ..`... ..`   ..   .:,    .. ::  .::,     .:,`   
   ,::    :::::::  ::, :::::::  `:::::::.,:: :::  ::: .::::::  ::::: ::::::  .::::::  
   ,::    :::::::: ::, :::::::: ::::::::.,:: :::  ::: :::,:::, ::::: ::::::, :::::::: 
   ,::    :::  ::: ::, :::  :::`::.  :::.,::  ::,`::`:::   ::: :::  `::,`   :::   ::: 
   ,::    ::.  ::: ::, ::`  :::.::    ::.,::  :::::: ::::::::: ::`   :::::: ::::::::: 
   ,::    ::.  ::: ::, ::`  :::.::    ::.,::  .::::: ::::::::: ::`    ::::::::::::::: 
   ,::    ::.  ::: ::, ::`  ::: ::: `:::.,::   ::::  :::`  ,,, ::`  .::  :::.::.  ,,, 
   ,::    ::.  ::: ::, ::`  ::: ::::::::.,::   ::::   :::::::` ::`   ::::::: :::::::. 
   ,::    ::.  ::: ::, ::`  :::  :::::::`,::    ::.    :::::`  ::`   ::::::   :::::.  
                                ::,  ,::                               ``             
                                ::::::::                                              
                                 ::::::                                               
                                  `,,`

https://www.thingiverse.com/thing:2939210
Parametric customizable cable gland (fitting) v. 4 by vimamsa is licensed under the Creative Commons - Attribution license.
http://creativecommons.org/licenses/by/3.0/

# Summary

Version 4 of the cable gland consists in a split in half bolt design with alignment notches, inside grip texture and a mounting nut. The default (and STL) size is 8 mm inner diameter and 12 mm outer diameter. Can be customized with OpenSCAD. The main advantages of this version are:

- Simple, robust and scalable design
- Fully customizable in OpenSCAD
- Complete 3d printed solution, no need of additional hardware parts
- Easy to print as is, without supports
- Easy to mount thanks to the split in half design, alignment notches and mounting nut
- Inside texture provides better grip

# Print Settings

Supports: No
Resolution: 0.2
Infill: 100%

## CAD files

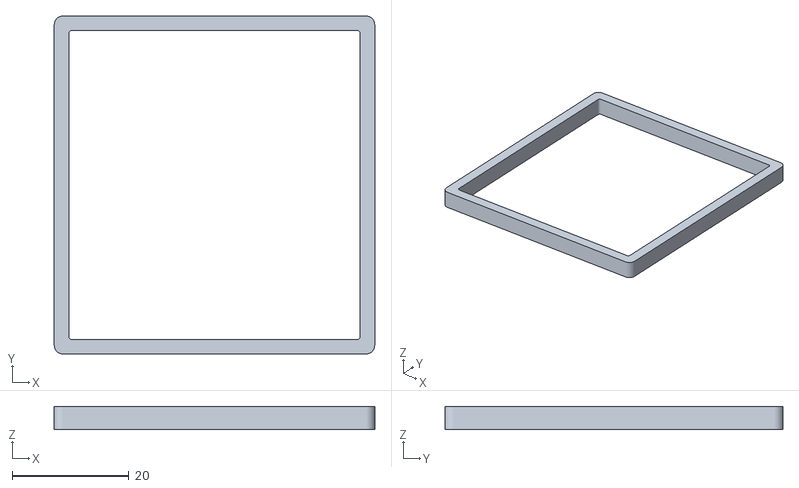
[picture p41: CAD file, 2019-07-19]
openSCAD/drop_oring.stl
55.0 x 58.0 x 4.00

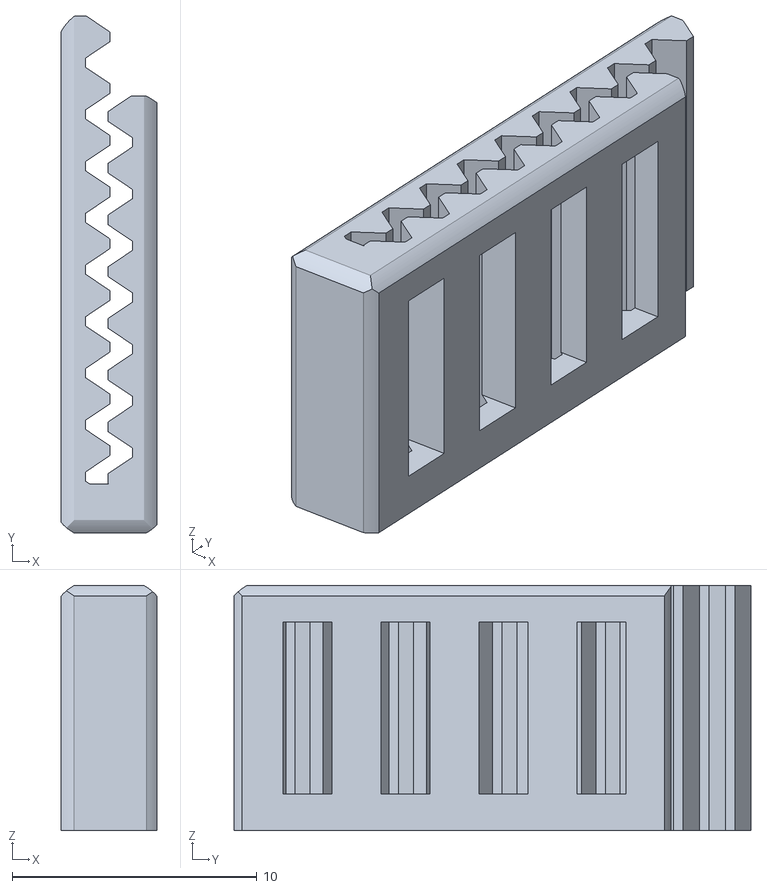
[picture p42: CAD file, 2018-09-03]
stl/16_mm_ribbon_cable_clip_v1.stl
3.91 x 21.1 x 10.0

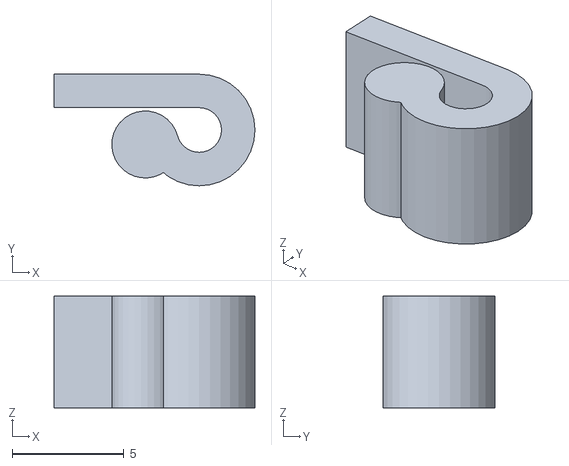
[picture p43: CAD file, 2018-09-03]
stl/3C_Cable_Clip_Customizable/files/cable-clip_flap_2mm_105_opening_angle.stl
9.00 x 5.00 x 5.00

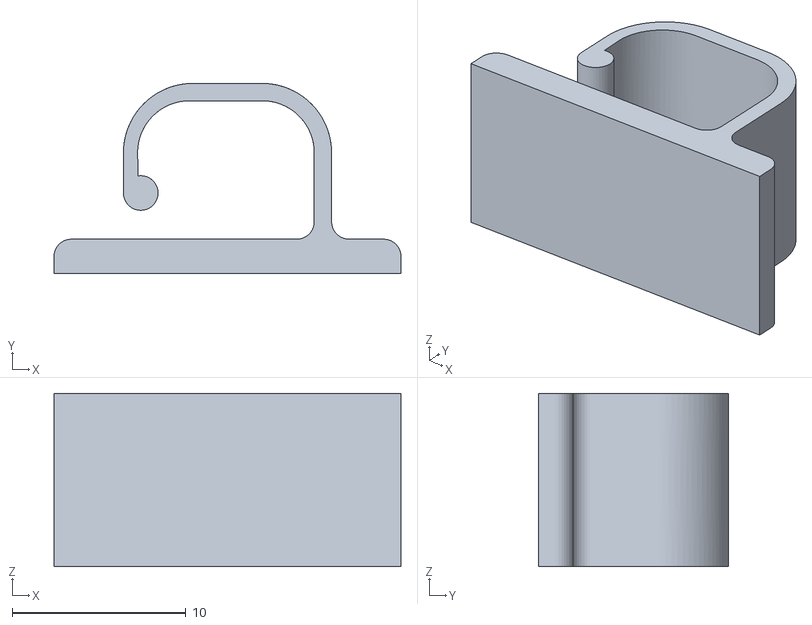
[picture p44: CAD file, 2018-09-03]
stl/Cable_Clip/files/CableClip.stl
20.0 x 11.0 x 10.0

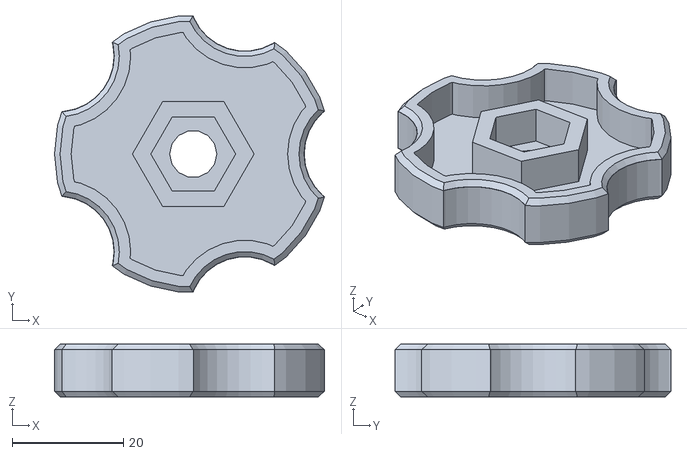
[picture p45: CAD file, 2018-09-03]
stl/Customizable_Thumb_Knob_-_Metric/Thumb_Knob_-_Alpha_-_Example.stl
48.6 x 49.7 x 9.50

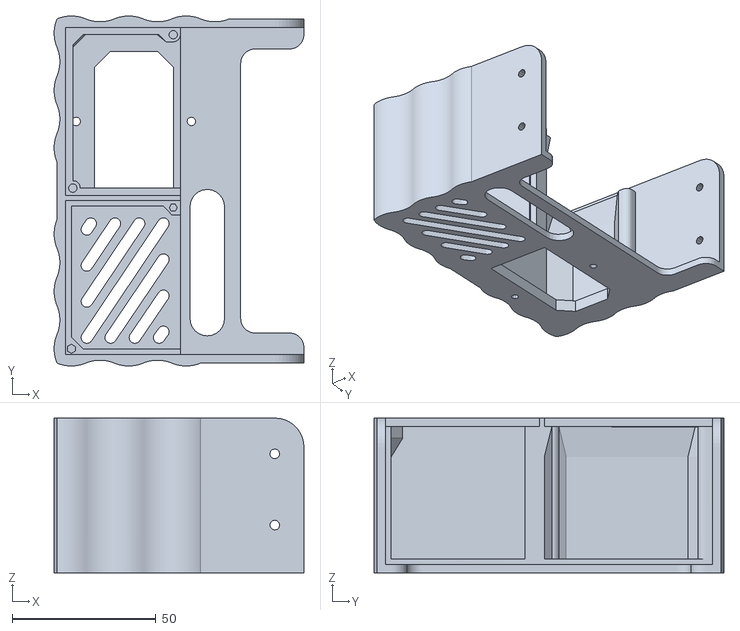
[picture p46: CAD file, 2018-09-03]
stl/LED_Style_Power_Supply_Cover/pwr_shield4.stl
87.0 x 121.9 x 53.9

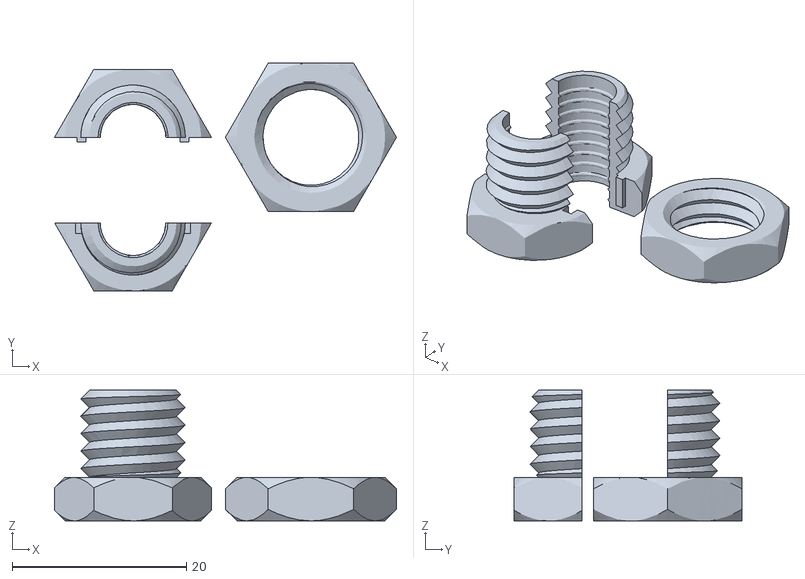
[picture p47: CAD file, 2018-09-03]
stl/Parametric_customizable_cable_gland_fitting_v._4/files/gland04_JM_id_8_od_12_hex.stl
39.2 x 26.1 x 15.0

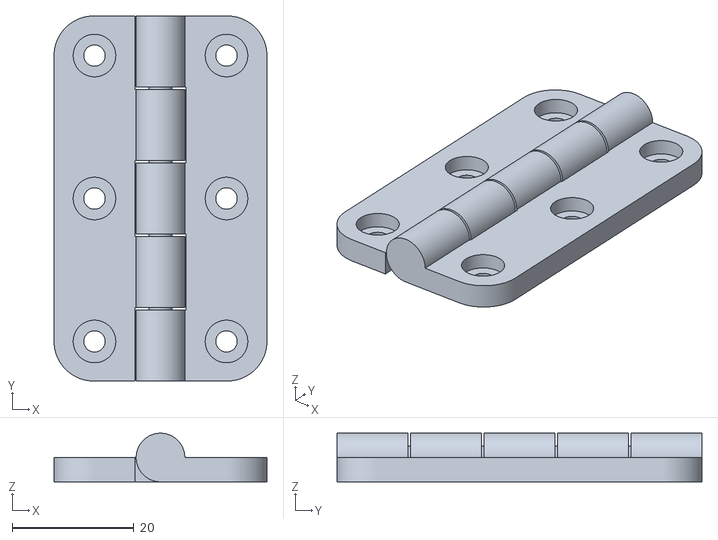
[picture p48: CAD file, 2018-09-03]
stl/Parametric_Hinge/files/parametric_butt_hinge_3.5.2_edit.stl
35.0 x 60.0 x 8.00

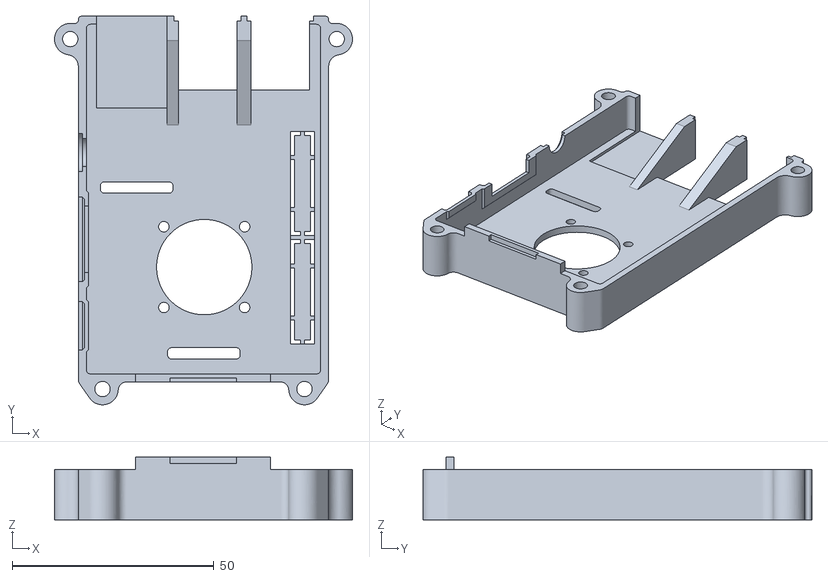
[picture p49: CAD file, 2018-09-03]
stl/Raspberry_Pi_3_Pi_2_and_Model_B+_case_with_VESA_mounts_and_more/files/rpi2-top_25mm-fan_netfabb.stl
73.8 x 96.2 x 15.5

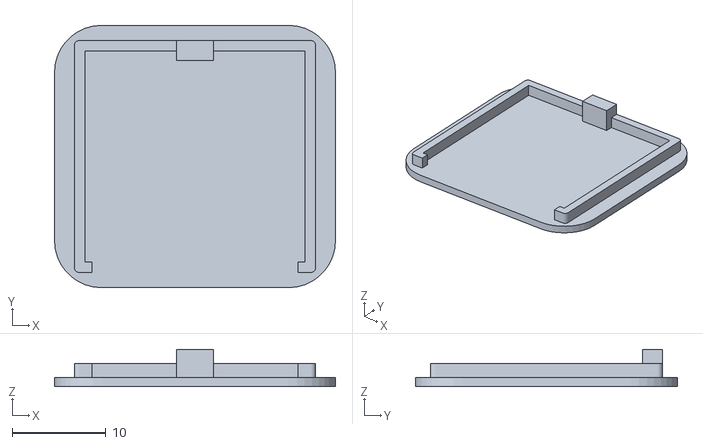
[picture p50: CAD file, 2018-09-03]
stl/RPi_camera_stand/RPi_camera_back.stl
30.0 x 28.0 x 4.00

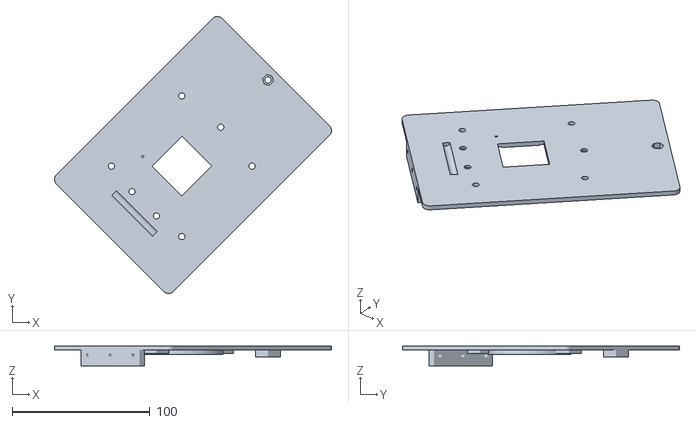
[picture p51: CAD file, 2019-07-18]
openSCAD/peltier_clamp2.stl
200.9 x 200.9 x 14.5

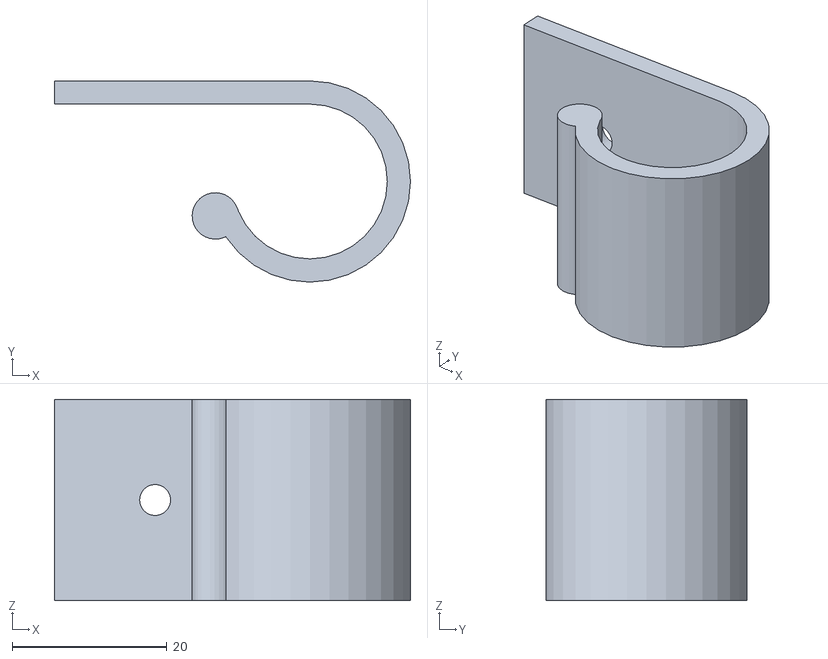
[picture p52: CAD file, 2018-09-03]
stl/3C_Cable_Clip_Customizable/files/cable-clip_flap_20mm.stl
46.0 x 26.0 x 26.0

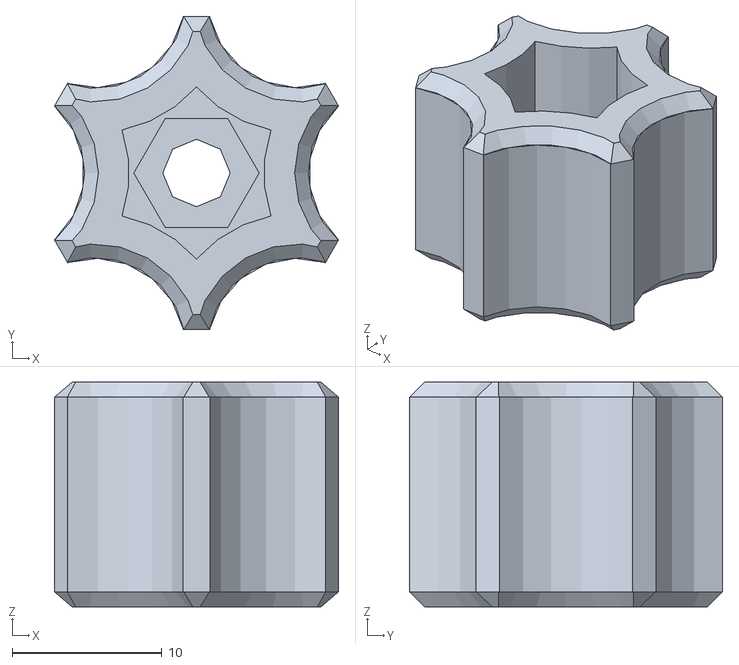
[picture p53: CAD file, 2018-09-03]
stl/Customizable_Thumb_Knob_-_Metric/Thumb_Knob_Custom_m4.stl
19.0 x 20.9 x 15.0

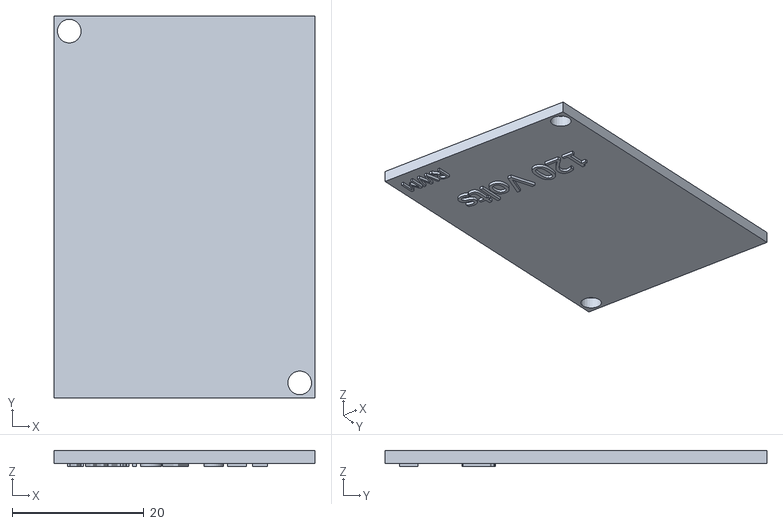
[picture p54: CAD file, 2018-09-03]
stl/LED_Style_Power_Supply_Cover/HVplate.stl
39.6 x 58.1 x 2.50

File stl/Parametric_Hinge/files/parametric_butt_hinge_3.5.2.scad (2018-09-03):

// -------------------------------------+---------------------------------------+---------------------------------------+---------------------------------------
// Title:        Parametric Butt Hinge
// Version:      3.5.2
// Release Date: 2017-05-26 (ISO)
// Author:       Rohin Gosling
// -------------------------------------+---------------------------------------+---------------------------------------+---------------------------------------
//
// Description:
//
// - Parametric butt hinge, designed to be printed in one step.
//
// - While the entire working hinge may be printed in one step, it is also possible to disabled the internal fused pin, and leave a shaft
//   which may be used in the case where an external pin is desired.
//
// Release Notes:
//
// - Version 3.5.2
//   * Removed extended ASCII characters to make the source code compatible with the UTF-8 encoding required by the Thingiverse Customizer.
//
// - Version 3.5
//   * For hexagonal counterbores, the hexagonal cut has been rotated 90 degrees, to reduce the need for support material.
//     The overhang angle for hexagonal counterbore is 60 degrees.
//
// - Version 3.4
//   * Added support for linear and parabolic gusset curves.
//   * Factored out all SCG (Solid Constructive Geometry) overlap constants, and consolidated them into one global constant, "SCG_OVERLAP".
//
// - Version 3.3
//   * Placed pin shaft parameters into their own parameter group in the Thingiverse Customizer.
//
// - Version 3.2
//   * Added support for independently configurable top and bottom pin shaft counterbores.
//   * Added an assembly option to flip the model about the z-axis. 
//     Usefull for viewing the top and bottom pin shaft counterbores.
//   * Configured the hinge throw angle Thingiverse Customizer parameter step size, to 5 degrees.
//
// - Version 3.1
//   * Added a counterbore feature for the pin shaft.
//     - While this feature may be enabled for one piece hinges that have the fused pin enabled, it is primarily designed for use with two
//       piece configurations that have their pin disabled. For instance, when the hinge is to be assembled using an external pin.
//     - In the case where a hinge is to be assembled using an external pin, it may be desired to have a pin shaft counterbore, where the end
//       caps of the knuckle joint array are counterbored, in order to allow the pin or bolt heads of the pin shaft, to be set flush with the
//       top and bottom edges of the hinge leaves.
//     - To accommodate both hexagonal and square bolt heads and nuts, the counterbore may be set to any one of circular, square or hexagonal.
//   * Added private text feature.
//     - A public parameter for the Thingiverse Customizer has not been added yet, however, users may set the 'text_enabled' local variable
//       in the 'leaf' module to 'true', which will enable a single row of inscribed text on each leaf.
//     - By default this feature will only work when exactly 4 fastener holes have been selected via the 'fastener_count' parameter, simply
//       because there is a nice open space available between the fastener holes for placing text, when 4 fastener holes are chosen.
//     - Text for the male and female leaves may be specified independently.
//
// - Version 3.0
//   * Added a parameter to disable the hinge pin, for when users would like to assemble with an external pin.
//   * Changed the main Thingiverse Customizer parameter group name from "Hinge Options", to "Assembly Options".
//   * Added a parameter to set the hinge throw angle.
//     Users can now set the throw angle, either for analysis and visualisation purposes, or for when the hinge is to be printed vertically
//     standing up on edge, in which case a throw angle of 120 degrees may be used to help keep the hinge stable on the build plate.
//   * Corrected spelling errors in the comments.
//
// - Version 2.9
//   * Added support for parabolic knuckle gussets to strengthen the knuckle joints.
//     Knuckle gussets may now be toggled on and off with the 'enable_knuckle_gusset' parameter.
//
// - Version 2.8
//   * Added the parameter, 'fastener_column_count', to enable single column fastener arrangements, that can be used for
//     piano hinge style fastener arrangements.
//
// - Version 2.7
//   * Rewrote the knuckle cutter module using mode generic math, that enables more parametizable control over knuckle joint 
//     dimensions and configuration.
//
// - Version 2.6
//   * Added support for countersunk fastener holes. Now users can select either counterbore or countersunk. 
//     dimensions and configuration.
//   * Started tracking release updates.
//
// - Version 1.0 - 2.5
//   * N/A - Release updates not tracked.
//
// -------------------------------------+---------------------------------------+---------------------------------------+---------------------------------------

// -------------------------------------+---------------------------------------+---------------------------------------+---------------------------------------
// Constants:
// -------------------------------------+---------------------------------------+---------------------------------------+---------------------------------------

// System constants.

C_CONSTANT = 0 + 0;     // Used to hide constant values from Thingiverse. Add to other constants to hide them as well.
C_NONE     = C_CONSTANT + 0;

// Leaf gender.

C_FEMALE   = C_CONSTANT + 0;
C_MALE     = C_CONSTANT + 1;

// SCG constants.

SCG_OVERLAP = C_CONSTANT + 0.01;    // Used for overlapping Boolean operations in order to avoid Boolean edge artefacts.
C_NEGATIVE  = C_CONSTANT + 0;       // Used for subtractive Boolean tools.
C_POSITIVE  = C_CONSTANT + 1;       // Used for additive Boolean tools.

// Bolt head shapes.

C_CIRCULAR  = C_CONSTANT + 0;
C_SQUARE    = C_CONSTANT + 1;
C_HEXAGONAL = C_CONSTANT + 2;

// Curve Type

C_FUNCTION_LINEAR    = C_CONSTANT + 1;      //   y = a*x + b
C_FUNCTION_CIRCULAR  = C_CONSTANT + 2;      // r^2 = x^2 + y^2 
C_FUNCTION_PARABOLIC = C_CONSTANT + 3;      //   y = (a^2)*(x - j)^2 + k    ...Vertex form.

// Minimum and maximum constraints.

C_MIN_HINGE_WIDTH                          = C_CONSTANT + 1.0;
C_MIN_HINGE_HEIGHT                         = C_CONSTANT + 1.0;
C_MIN_LEAF_GAUGE                           = C_CONSTANT + 1.0;
C_MIN_COMPONENT_CLEARENCE                  = C_CONSTANT + 0.1;
C_MAX_COMPONENT_CLEARENCE                  = C_CONSTANT + 1.0;
C_MIN_KNUCKLE_COUNT                        = C_CONSTANT + 3;
C_MAX_KNUCKLE_COUNT                        = C_CONSTANT + 15;
C_MIN_KNUCKLE_GUSSET_WIDTH                 = C_CONSTANT + 1.0; 
C_MIN_FASTENER_MARGIN                      = C_CONSTANT + 1.0; 
C_MIN_PIN_DIAMETER                         = C_CONSTANT + 1.0; 
C_MIN_COUNTER_SINK_DEPTH_STOP              = C_CONSTANT + 1.0; 
C_MIN_FASTENER_THREAD_DIAMETER             = C_CONSTANT + 0.0; 
C_MIN_FASTENER_COUNT                       = C_CONSTANT + 3; 
C_MIN_FASTENER_COLUMN_COUNT                = C_CONSTANT + 1; 
C_MAX_FASTENER_COLUMN_COUNT                = C_CONSTANT + 2; 
C_MIN_TESSELLATION                         = C_CONSTANT + 32; 
C_MAX_TESSELLATION                         = C_CONSTANT + 256;
C_MIN_THROW_ANGLE                          = C_CONSTANT + -90;
C_MAX_THROW_ANGLE                          = C_CONSTANT + 180;
C_DEFAULT_THROW_ANGLE                      = C_CONSTANT + 0;
C_MIN_PIN_SHAFT_COUNTERBORE_DIAMETER       = C_CONSTANT + 0.1;
C_MIN_PIN_SHAFT_COUNTERBORE_WALL_THICKNESS = C_CONSTANT + 0.3;
C_MIN_PIN_SHAFT_COUNTERBORE_DEPTH          = C_CONSTANT + 0.0;


// -------------------------------------+---------------------------------------+---------------------------------------+---------------------------------------
// Thingiverse Parameters.
//
// - These parameters are used to integrate with the Thingiverse Customizer, and should only be used by the
//   class member variables specified in the "Model parameters" section below.
//
// - These Thingiverse Parameters should never be accessed from inside any module. We do this to enforce 
//   principles of object orientation.
//
// - By separating concerns between variables exposed to Thingiverse vs. variables used internally by the 
//   SCAD model (class), we are better able to manage the ordering and grouping of variables exposed to 
//   Thingiverse, vs. the ordering of variables used internally by the model.
//
// -------------------------------------+---------------------------------------+---------------------------------------+---------------------------------------

/* [Assembly Options] */
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

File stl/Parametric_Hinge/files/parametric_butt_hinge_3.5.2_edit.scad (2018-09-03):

// -------------------------------------+---------------------------------------+---------------------------------------+---------------------------------------
// Title:        Parametric Butt Hinge
// Version:      3.5.2
// Release Date: 2017-05-26 (ISO)
// Author:       Rohin Gosling
// -------------------------------------+---------------------------------------+---------------------------------------+---------------------------------------
//
// Description:
//
// - Parametric butt hinge, designed to be printed in one step.
//
// - While the entire working hinge may be printed in one step, it is also possible to disabled the internal fused pin, and leave a shaft
//   which may be used in the case where an external pin is desired.
//
// Release Notes:
//
// - Version 3.5.2
//   * Removed extended ASCII characters to make the source code compatible with the UTF-8 encoding required by the Thingiverse Customizer.
//
// - Version 3.5
//   * For hexagonal counterbores, the hexagonal cut has been rotated 90 degrees, to reduce the need for support material.
//     The overhang angle for hexagonal counterbore is 60 degrees.
//
// - Version 3.4
//   * Added support for linear and parabolic gusset curves.
//   * Factored out all SCG (Solid Constructive Geometry) overlap constants, and consolidated them into one global constant, "SCG_OVERLAP".
//
// - Version 3.3
//   * Placed pin shaft parameters into their own parameter group in the Thingiverse Customizer.
//
// - Version 3.2
//   * Added support for independently configurable top and bottom pin shaft counterbores.
//   * Added an assembly option to flip the model about the z-axis. 
//     Usefull for viewing the top and bottom pin shaft counterbores.
//   * Configured the hinge throw angle Thingiverse Customizer parameter step size, to 5 degrees.
//
// - Version 3.1
//   * Added a counterbore feature for the pin shaft.
//     - While this feature may be enabled for one piece hinges that have the fused pin enabled, it is primarily designed for use with two
//       piece configurations that have their pin disabled. For instance, when the hinge is to be assembled using an external pin.
//     - In the case where a hinge is to be assembled using an external pin, it may be desired to have a pin shaft counterbore, where the end
//       caps of the knuckle joint array are counterbored, in order to allow the pin or bolt heads of the pin shaft, to be set flush with the
//       top and bottom edges of the hinge leaves.
//     - To accommodate both hexagonal and square bolt heads and nuts, the counterbore may be set to any one of circular, square or hexagonal.
//   * Added private text feature.
//     - A public parameter for the Thingiverse Customizer has not been added yet, however, users may set the 'text_enabled' local variable
//       in the 'leaf' module to 'true', which will enable a single row of inscribed text on each leaf.
//     - By default this feature will only work when exactly 4 fastener holes have been selected via the 'fastener_count' parameter, simply
//       because there is a nice open space available between the fastener holes for placing text, when 4 fastener holes are chosen.
//     - Text for the male and female leaves may be specified independently.
//
// - Version 3.0
//   * Added a parameter to disable the hinge pin, for when users would like to assemble with an external pin.
//   * Changed the main Thingiverse Customizer parameter group name from "Hinge Options", to "Assembly Options".
//   * Added a parameter to set the hinge throw angle.
//     Users can now set the throw angle, either for analysis and visualisation purposes, or for when the hinge is to be printed vertically
//     standing up on edge, in which case a throw angle of 120 degrees may be used to help keep the hinge stable on the build plate.
//   * Corrected spelling errors in the comments.
//
// - Version 2.9
//   * Added support for parabolic knuckle gussets to strengthen the knuckle joints.
//     Knuckle gussets may now be toggled on and off with the 'enable_knuckle_gusset' parameter.
//
// - Version 2.8
//   * Added the parameter, 'fastener_column_count', to enable single column fastener arrangements, that can be used for
//     piano hinge style fastener arrangements.
//
// - Version 2.7
//   * Rewrote the knuckle cutter module using mode generic math, that enables more parametizable control over knuckle joint 
//     dimensions and configuration.
//
// - Version 2.6
//   * Added support for countersunk fastener holes. Now users can select either counterbore or countersunk. 
//     dimensions and configuration.
//   * Started tracking release updates.
//
// - Version 1.0 - 2.5
//   * N/A - Release updates not tracked.
//
// -------------------------------------+---------------------------------------+---------------------------------------+---------------------------------------

// -------------------------------------+---------------------------------------+---------------------------------------+---------------------------------------
// Constants:
// -------------------------------------+---------------------------------------+---------------------------------------+---------------------------------------

// System constants.

C_CONSTANT = 0 + 0;     // Used to hide constant values from Thingiverse. Add to other constants to hide them as well.
C_NONE     = C_CONSTANT + 0;

// Leaf gender.

C_FEMALE   = C_CONSTANT + 0;
C_MALE     = C_CONSTANT + 1;

// SCG constants.

SCG_OVERLAP = C_CONSTANT + 0.01;    // Used for overlapping Boolean operations in order to avoid Boolean edge artefacts.
C_NEGATIVE  = C_CONSTANT + 0;       // Used for subtractive Boolean tools.
C_POSITIVE  = C_CONSTANT + 1;       // Used for additive Boolean tools.

// Bolt head shapes.

C_CIRCULAR  = C_CONSTANT + 0;
C_SQUARE    = C_CONSTANT + 1;
C_HEXAGONAL = C_CONSTANT + 2;

// Curve Type

C_FUNCTION_LINEAR    = C_CONSTANT + 1;      //   y = a*x + b
C_FUNCTION_CIRCULAR  = C_CONSTANT + 2;      // r^2 = x^2 + y^2 
C_FUNCTION_PARABOLIC = C_CONSTANT + 3;      //   y = (a^2)*(x - j)^2 + k    ...Vertex form.

// Minimum and maximum constraints.

C_MIN_HINGE_WIDTH                          = C_CONSTANT + 1.0;
C_MIN_HINGE_HEIGHT                         = C_CONSTANT + 1.0;
C_MIN_LEAF_GAUGE                           = C_CONSTANT + 1.0;
C_MIN_COMPONENT_CLEARENCE                  = C_CONSTANT + 0.1;
C_MAX_COMPONENT_CLEARENCE                  = C_CONSTANT + 1.0;
C_MIN_KNUCKLE_COUNT                        = C_CONSTANT + 3;
C_MAX_KNUCKLE_COUNT                        = C_CONSTANT + 15;
C_MIN_KNUCKLE_GUSSET_WIDTH                 = C_CONSTANT + 1.0; 
C_MIN_FASTENER_MARGIN                      = C_CONSTANT + 1.0; 
C_MIN_PIN_DIAMETER                         = C_CONSTANT + 1.0; 
C_MIN_COUNTER_SINK_DEPTH_STOP              = C_CONSTANT + 1.0; 
C_MIN_FASTENER_THREAD_DIAMETER             = C_CONSTANT + 0.0; 
C_MIN_FASTENER_COUNT                       = C_CONSTANT + 3; 
C_MIN_FASTENER_COLUMN_COUNT                = C_CONSTANT + 1; 
C_MAX_FASTENER_COLUMN_COUNT                = C_CONSTANT + 2; 
C_MIN_TESSELLATION                         = C_CONSTANT + 32; 
C_MAX_TESSELLATION                         = C_CONSTANT + 256;
C_MIN_THROW_ANGLE                          = C_CONSTANT + -90;
C_MAX_THROW_ANGLE                          = C_CONSTANT + 180;
C_DEFAULT_THROW_ANGLE                      = C_CONSTANT + 0;
C_MIN_PIN_SHAFT_COUNTERBORE_DIAMETER       = C_CONSTANT + 0.1;
C_MIN_PIN_SHAFT_COUNTERBORE_WALL_THICKNESS = C_CONSTANT + 0.3;
C_MIN_PIN_SHAFT_COUNTERBORE_DEPTH          = C_CONSTANT + 0.0;


// -------------------------------------+---------------------------------------+---------------------------------------+---------------------------------------
// Thingiverse Parameters.
//
// - These parameters are used to integrate with the Thingiverse Customizer, and should only be used by the
//   class member variables specified in the "Model parameters" section below.
//
// - These Thingiverse Parameters should never be accessed from inside any module. We do this to enforce 
//   principles of object orientation.
//
// - By separating concerns between variables exposed to Thingiverse vs. variables used internally by the 
//   SCAD model (class), we are better able to manage the ordering and grouping of variables exposed to 
//   Thingiverse, vs. the ordering of variables used internally by the model.
//
// -------------------------------------+---------------------------------------+---------------------------------------+---------------------------------------

/* [Assembly Options] */
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

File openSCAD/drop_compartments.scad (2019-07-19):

COMPARTMENTS=1;
ORING_ONLY=2;

version1=ORING_ONLY;

$fn=60;
union() {
    difference() {
        minkowski() {
            cube([55-3,58-3,2.],true);
            cylinder(d=3,h=2.,center=true);
        }
        minkowski() {
            cube([50-1,53-1,5.1],true);
            cylinder(d=1,h=2.5,center=true);
        }
        
    }
    if(version1==COMPARTMENTS) {
        difference() {
            union() {
                translate([0,0,0.4]) minkowski() {
                    cube([24.2-5,26-5,3.2/2.],true);
                    cylinder(d=5,h=3.2/2.,center=true);
                }
                translate([0,0,1-0.5]) cube([55,2.5,3],true);
                translate([0,0,1-0.5]) cube([2.5,55,3],true);
            }
            
            
            translate([0,0,-2-0.5-0.3]) cube([25.2,25.2,2],true);
            for (i=[1 : 4]) {
                for(j=[1:4]) {
                    translate([-25/2+4+(25-2)/4*(i-1),
                        -25/2+4+(25-2)/4*(j-1),0]) cylinder(d=5.,h=10,center=true);
                }   
            }
            
        }
    }
}

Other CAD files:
stl/Raspberry_Pi_3_Pi_2_and_Model_B+_case_with_VESA_mounts_and_more/files/rpi3-bottom_netfabb.stl
stl/RPi_camera_stand/RPi_camera_stand.stl
openSCAD/drop_compartments.stl
stl/3C_Cable_Clip_Customizable/files/cable-clip-5.5mm-7.5mm-twisted-45deg.stl
openSCAD/enclosure_cam.scad
openSCAD/enclosure_cam_box.stl
openSCAD/enclosure_cam_lid.stl
openSCAD/enclosure_cam_lid2.stl
openSCAD/fan_guard.scad
openSCAD/fan_guard.stl
openSCAD/feet.scad
openSCAD/feet.stl
openSCAD/fixing.stl
openSCAD/oring_placement.stl
openSCAD/peltier_clamp.stl
openSCAD/touchscreen_clamp.scad
openSCAD/touchscreen_clamp.stl
openSCAD/touchscreen_mount.scad
openSCAD/touchscreen_mount_l.stl
openSCAD/touchscreen_mount_r.stl
stl/3C_Cable_Clip_Customizable/files/cable-clip-5.5mm-7.5mm-2nd-variant.stl
stl/3C_Cable_Clip_Customizable/files/cable-clip-5.5mm-7.5mm-twisted-90deg.stl
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

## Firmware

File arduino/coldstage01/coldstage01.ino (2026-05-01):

#include <util/atomic.h>

#include <Wire.h> // for i2c communication between RPi and Arduino
#include <PID_v1.h> // for PID control by Arduino

#define ADDRESS 0x04
#define sampletime 1000 // time for printing to Serial 
#define rpi true
#define writeserial false
#define FLOATS_SENT 1 // number of floating-point variables sent to RPi
#define high_freq true
float factor = 1.; // was 62
#define MPIN 6

volatile float data_s[FLOATS_SENT]; // buffer to send variables to RPi
volatile float tstore=0.;
volatile float tstore2;
byte data[12]; // buffer to read variables sent from RPi (as bytes)
int command,potVal;

unsigned long  starttime,newmillis,starttime2,newmillis2; // variable to determine when Serial IO occurs




/* ++++++++++++++++++++++++++++++++++++++++++++++++++++++++++++++++++
 variables for PID https://playground.arduino.cc/Code/PIDLibaryBasicExample
   ++++++++++++++++++++++++++++++++++++++++++++++++++++++++++++++++++
 */
volatile float temperature_read = 0.0,Setpoint=100.0, Output, OutputC; // set point initially high, so current off
volatile float temperature_pid = 0.0;
volatile int numr=0,numrs=0;
#define OUTPUT_MIN 235
#define OUTPUT_MAX 5
//PID myPID((double *) &temperature_read, (double *) &Output,
//  (double *) &Setpoint, 2, 5, 1, P_ON_E, REVERSE);

// tuned at 5 C using Ziegler-Nichols method
// http://www.pcbheaven.com/wikipages/PID_Theory/?p=1
// set i and d to zero, slowly increase kc
//  until oscillation centered about set-point
// note period of oscillation in seconds - this is pc
/*#define pc 30. // seconds
#define kc 21. // critical gain
PID myPID((double *) &temperature_pid, (double *) &Output,
  (double *) &Setpoint, 0.6*kc/15.0, 0.5*pc, pc/8., P_ON_M, REVERSE);*/
/*#define kp 0.18
#define ki 0.015
#define kd 0.0*/

#define kpw 13.5
#define kiw 0.7
#define kdw 0.0

#define kpc kpw
#define kic kiw
#define kdc kdw

PID myPID((double *) &temperature_pid, (double *) &Output,
  (double *) &Setpoint, kpw,kiw,kdw, P_ON_E, REVERSE);
/* ------------------------------------------------------------------
*/

void setup ()
{
  
  Serial.begin(9600);
  Serial.println("Peltier Controller Code for Cold Stage 001 (2026-04-03)");
  
  pinMode(MPIN, OUTPUT); // output pin for OCR2B
  pinMode(5,INPUT);
  pinMode(4,INPUT);
  pinMode(A1,INPUT); // pot read

  if(high_freq) {
    /*TCCR0B=TCCR0B & B11111000 | B00000001; // set timer 0 divisor to     1 for PWM frequency of 62500.00 Hz
    factor=62.; // shoudl be 64 */
    //TCCR1B = TCCR1B & B11111000 | B00000001; // set timer 1 divisor to     1 for PWM frequency of 31371.55 Hz
    /*factor=31.;
    TCCR0A = _BV(COM0A1) | _BV(COM0B1) | _BV(WGM01) | _BV(WGM00);
    TCCR0B = _BV(CS01); // Prescaler 8 -> 16MHz / (8 * 64) = 31.25kHz*/

    // 7.8kHz
    /*TCCR0B = (TCCR0B & B11111000) | B00000010;
    factor = 8.;*/
    // 1kHz
    TCCR0B = (TCCR0B & B11111000) | B00000011;
    factor = 1.;
} 
    
  starttime = millis()/factor;   // get the current time;
  starttime2 = millis()/factor;   // get the current time;

  // turn PID on
  myPID.SetMode(AUTOMATIC);
  myPID.SetOutputLimits(OUTPUT_MAX, OUTPUT_MIN);
  myPID.SetSampleTime(100*factor);
  data_s[0]=0.;
  // read the temperature
  readTemp();


  
  // i2c comms
  Wire.begin(ADDRESS);
  Wire.onReceive(receiveEvent); // Register event: receive set point from RPi
  Wire.onRequest(sendData); // send temperature to RPi
}





void readTemp() {
  int value;
  /* ++++++++++++++++++++++++++++++++++++++++++++++++++++++++++++++++++
   * AD8495 thermocouple
   * ++++++++++++++++++++++++++++++++++++++++++++++++++++++++++++++++++
  */
  value=analogRead(A7);
//  temperature_read=(float(value)/1023.*5.)*203.5837-508.7424;
//  temperature_read=float(value)*1.0528-540.5262;
// temperature_read=(float(value)/1023.*5.-1.25)/5.e-3-6.3;
// temperature_read=float(value)*1.078988 - 278.587;
 temperature_read=float(value)*1.06892327 - 273.38273772;
 
// low-pass filter
temperature_pid = 0.9*temperature_pid + 0.1*temperature_read; //Serial.println(value);

  ATOMIC_BLOCK(ATOMIC_RESTORESTATE)
  {    
      numr++;
      data_s[0]+=temperature_read;
  }
  ATOMIC_BLOCK(ATOMIC_RESTORESTATE)
  {    
      tstore+=temperature_read;
      numrs++;
  }
}




void loop ()
{
  int mosfetSwitch, usePot, value;

  // read the temperature
  readTemp();
  
  newmillis = millis()/factor;
  /* ++++++++++++++++++++++++++++++++++++++++++++++++++++++++++++++++++
   * Power to Peltier
   * ++++++++++++++++++++++++++++++++++++++++++++++++++++++++++++++++++
  */
  mosfetSwitch=digitalRead(4); 
  if(mosfetSwitch==LOW) { // turn off current to Peltier
    analogWrite(6,0);
  } else {                // turn on current to Peltier
    usePot=digitalRead(5);
    if(usePot == LOW) {   // default set-point for PWM to 
                          // buck converter / Peltier

       if(rpi) {
        if (Setpoint > -20.0) {
          myPID.SetTunings(kpw,kiw,kdw);
        } else {
          myPID.SetTunings(kpc,kic,kdc);
        }
        //temperature_read=data_s[0] / numr;
        myPID.Compute(); // call every loop, updates automatically at the time interval set
        OutputC = Output;
        OutputC=min(OutputC,OUTPUT_MIN);
        OutputC=max(OutputC,OUTPUT_MAX);
        if(isnan(OutputC)) OutputC = 0.;
        if(Setpoint > 50.) OutputC = 0.;
        analogWrite(MPIN,OutputC);
        //Serial.println(Output);
        //delay(500*factor);
      } else {
        analogWrite(MPIN,200); 
      }
    } else {              // use potential divider to 
                          // determine PWM for buck converter / Peltier
      potVal=analogRead(A1);
      potVal=map(potVal,0,1023,0,OUTPUT_MIN);
      potVal=min(potVal,OUTPUT_MIN);
      analogWrite(MPIN,potVal);
    }
    //delay(100*factor);
  }
  /* ------------------------------------------------------------------
  */
  /*newmillis2=millis()/factor;
  if((newmillis2-starttime2 >= sampletime)) {
    float temp;
    Serial.print("Temperature is ");
    temp=tstore / numrs;
    Serial.print(temp);
    Serial.print("; Output is ");
    Serial.print(Output);
    Serial.println("");
    starttime2=millis()/factor;
    tstore=0.;
    numrs=0;
  }*/






}



/* ++++++++++++++++++++++++++++++++++++++++++++++++++++++++++++++++++
 * Parse values that have been read in, into a float
 * in this case the set point temperature
 * ++++++++++++++++++++++++++++++++++++++++++++++++++++++++++++++++++
*/
void parseValues(byte data[]) {
  union float_tag {
    byte b[4];
    float fval;
  } ft;
  ft.b[0] = data[2];
  ft.b[1] = data[3];
  ft.b[2] = data[4];
  ft.b[3] = data[5];

  if(!isnan(ft.fval)) Setpoint = float(ft.fval);
  
}
/* ------------------------------------------------------------------
*/



/* ++++++++++++++++++++++++++++++++++++++++++++++++++++++++++++++++++
 * Send data to RPi
 * ++++++++++++++++++++++++++++++++++++++++++++++++++++++++++++++++++
*/
void sendData(){
  /* ++++++++++++++++++++++++++++++++++++++++++++++++++++++++++++++++++
   * Serial 
   * ++++++++++++++++++++++++++++++++++++++++++++++++++++++++++++++++++
  */
  
  
  //if((newmillis-starttime) >= sampletime) {
//    data_s[0] /= numr;
    ATOMIC_BLOCK(ATOMIC_RESTORESTATE)
    {    
      tstore2=(float)data_s[0] / numr;

    byte *b = (byte*)&tstore2;
    uint8_t checksum = b[0] ^ b[1] ^ b[2] ^ b[3];
    Wire.write((uint8_t *) &tstore2, FLOATS_SENT*sizeof(float));
    Wire.write(checksum);      // send checksum byte
    
    data_s[0]=0.;
    numr=0;

#if writeserial
    Serial.print("Temperature is ");
    Serial.print(tstore2);
    Serial.print(" ");
    Serial.print(Setpoint);
    Serial.print(" ");
    Serial.print(Output);
    Serial.print(" ");
    Serial.print(starttime);
    Serial.print(" ");
    Serial.print(newmillis);
    Serial.println();
#endif

    starttime=newmillis;
//    delay(1*factor);
    }
  //}
  /* ------------------------------------------------------------------
  */
  //delay(1*factor);
}
/* ------------------------------------------------------------------
*/



/* ++++++++++++++++++++++++++++++++++++++++++++++++++++++++++++++++++
 * function that executes whenever data is received from master 
 * this function is registered as an event, see setup()
 * ++++++++++++++++++++++++++++++++++++++++++++++++++++++++++++++++++
*/
void receiveEvent1(int howMany)
{
  byte test, command=0,tmp;
  if(howMany == 0) return;
/*  while (command != 255) {
    command = Wire.read();
    Serial.println(command);
  }
  while (command != 1) {
    command = Wire.read();
    Serial.println(command);
  }*/
  //command = Wire.read();
  //if (command==1){
    int i=0;
    //if(howMany >= 4) {
      while(1 <= Wire.available()) // loop through all but the last
      {
        data[i] = Wire.read(); // receive byte as a character
        if(data[i] == 1) i=-1;
        i = i+1;
        //i=min(i,10);
      }
/*      Serial.print(data[0]);
      Serial.print(" ");
      Serial.print(data[1]);
      Serial.print(" ");
      Serial.print(data[2]);
      Serial.print(" ");
      Serial.print(data[3]);
      Serial.print(" ");
      Serial.print(data[4]);
      Serial.print(" ");*/
      parseValues(data);
   //}
   //myPID.SetTunings(0.6*kc, 0.5*pc, pc/8.);
} 

void receiveEvent(int howMany)
{
  int count = 0;

  while (Wire.available()) {
    byte b = Wire.read();

    if (count < 8) {
      data[count] = b;
    } else {
      // shift left and keep only the newest 8 bytes
      data[0] = data[1];
      data[1] = data[2];
      data[2] = data[3];
      data[3] = data[4];
      data[4] = data[5];
      data[5] = data[6];
      data[6] = data[7];
      data[7] = b;
    }
    count++;
  }

  // Ignore the 1-byte transaction sent before Pi reads
  if (count == 1 && data[0] == 0) return;

  // Expect the last 8 bytes to be: 1, 6, f0, f1, f2, f3, command, test
  if (count >= 8 && data[0] == 1 && data[1] == 6) {
    parseValues(data);
  }
}
/* ------------------------------------------------------------------
*/

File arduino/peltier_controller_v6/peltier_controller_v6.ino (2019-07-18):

#include <Wire.h> // for i2c communication between RPi and Arduino
#include <PID_v1.h> // for PID control by Arduino - Brett Beauregard
#include "Adafruit_MAX31855.h" // thermocouple

#define ADDRESS 0x04
#define sampletime 1000 // time for printing to Serial 
#define rpi true
#define FLOATS_SENT 1 // number of floating-point variables sent to RPi
#define high_freq true
float factor = 1.; // was 62
#define MPIN 6

// MAX31855
const int maxSO =  12;
const int maxCS = 11;
const int maxSCK = 10;
//Create a MAX31855 reference and tell it what pin does what
Adafruit_MAX31855 kTC(maxSCK, maxCS, maxSO);



float data_s[FLOATS_SENT]; // buffer to send variables to RPi
byte data[12]; // buffer to read variables sent from RPi (as bytes)
int command,potVal;

unsigned long  starttime,newmillis; // variable to determine when Serial IO occurs

/* ++++++++++++++++++++++++++++++++++++++++++++++++++++++++++++++++++
 variables for PID https://playground.arduino.cc/Code/PIDLibaryBasicExample
   ++++++++++++++++++++++++++++++++++++++++++++++++++++++++++++++++++
 */
double temperature_read = 0.0, Setpoint=100.0, Output; // set point initially high, so current off
int numr=0;
#define OUTPUT_MIN 235
#define OUTPUT_MAX 10
PID myPID(&temperature_read, &Output,&Setpoint, 2, 5, 1, P_ON_M, REVERSE);
/* ------------------------------------------------------------------
*/

void setup ()
{
  
  Serial.begin(9600);
  pinMode(MPIN, OUTPUT); // output pin for OCR2B
  pinMode(5,INPUT);
  pinMode(4,INPUT);
  pinMode(A1,INPUT); // pot read
  pinMode(9,OUTPUT);
  digitalWrite(9,HIGH);

  if(high_freq) {
    TCCR0B=TCCR0B & B11111000 | B00000001; // set timer 0 divisor to     1 for PWM frequency of 62500.00 Hz
    factor=62.;
    //TCCR1B = TCCR1B & B11111000 | B00000001; // set timer 1 divisor to     1 for PWM frequency of 31371.55 Hz
    //factor=32.;
  } 
    
  starttime = millis()/factor;   // get the current time;

  // turn PID on
  myPID.SetMode(AUTOMATIC);
  myPID.SetOutputLimits(OUTPUT_MIN, OUTPUT_MAX);
  myPID.SetSampleTime(200*factor);
  data_s[0]=0.;
  // read the temperature
  readTemp();
  // i2c comms
  Wire.begin(ADDRESS);
  Wire.onReceive(receiveEvent); // Register event: receive set point from RPi
  Wire.onRequest(sendData); // send temperature to RPi
}





void readTemp() {
  int value;
  /* ++++++++++++++++++++++++++++++++++++++++++++++++++++++++++++++++++
   * AD8495 thermocouple
   * ++++++++++++++++++++++++++++++++++++++++++++++++++++++++++++++++++
  */
//  value=analogRead(A0);
//  temperature_read=(float(value)/1023.*5.)*203.5837-508.7424;
//  temperature_read=float(value)*1.0528-540.5262;
  temperature_read=kTC.readCelsius();
  
  numr++;
  data_s[0]+=temperature_read;
  /* ------------------------------------------------------------------
  */
}




void loop ()
{
  int mosfetSwitch, usePot, value;

  // read the temperature
  readTemp();
  

  /* ++++++++++++++++++++++++++++++++++++++++++++++++++++++++++++++++++
   * Power to Peltier
   * ++++++++++++++++++++++++++++++++++++++++++++++++++++++++++++++++++
  */
  mosfetSwitch=digitalRead(4); 
  if(mosfetSwitch==LOW) { // turn off current to Peltier
    analogWrite(6,0);
  } else {                // turn on current to Peltier
    usePot=digitalRead(5);
    
    if(usePot == LOW) {   // default set-point for PWM to 
                          // buck converter / Peltier

      if(rpi) {
        //temperature_read=data_s[0] / numr;
        myPID.Compute(); // call every loop, updates automatically at the time interval set
        Output=min(Output,OUTPUT_MIN);
        Output=max(Output,OUTPUT_MAX);
        if(isnan(Output)) Output = 0.;
        if(Setpoint > 50.) Output = 0.;
        analogWrite(MPIN,Output);
        //Serial.println(Output);
        //delay(500*factor);
      } else {
        analogWrite(MPIN,200); 
      }
    } else {              // use potential divider to 
                          // determine PWM for buck converter / Peltier
      potVal=analogRead(A1);
      potVal=map(potVal,0,1023,0,235);
      potVal=min(potVal,235);
      analogWrite(MPIN,potVal);
    }
    //delay(100*factor);
  }
  /* ------------------------------------------------------------------
  */


    Serial.print("Temperature is ");
    Serial.print(temperature_read);
    Serial.print("; Output is ");
    Serial.print(Output);
    Serial.println("");







}



/* ++++++++++++++++++++++++++++++++++++++++++++++++++++++++++++++++++
 * Parse values that have been read in, into a float
 * in this case the set point temperature
 * ++++++++++++++++++++++++++++++++++++++++++++++++++++++++++++++++++
*/
void parseValues(byte data[]) {
  union float_tag {
    byte b[4];
    float fval;
  } ft;
  ft.b[0] = data[1];
  ft.b[1] = data[2];
  ft.b[2] = data[3];
  ft.b[3] = data[4];

  if(!isnan(ft.fval)) Setpoint = double(ft.fval);
  
}
/* ------------------------------------------------------------------
*/
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

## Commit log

2018-09-16 fixed temperature calibration, plus a few extra updates
    [enclosure_cam.scad, enclosure_cam_lid2.stl, gland04_JM.scad, touchscreen_clamp.scad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]
2019-07-18 python scripts updated and several other enhancements
    [drop_compartments.scad, drop_compartments.stl, fan_guard.scad, peltier_clamp2.stl]
2019-07-19 added o-ring stl file and edit to related scad file
    [drop_compartments.scad, drop_oring.stl]
2020-09-08 calibration of thermocouple based on 1st version of cold state (5a)
2023-05-25 calibration of coldstages and some renaming /tidying up
2026-05-01 new calibration with Angel
